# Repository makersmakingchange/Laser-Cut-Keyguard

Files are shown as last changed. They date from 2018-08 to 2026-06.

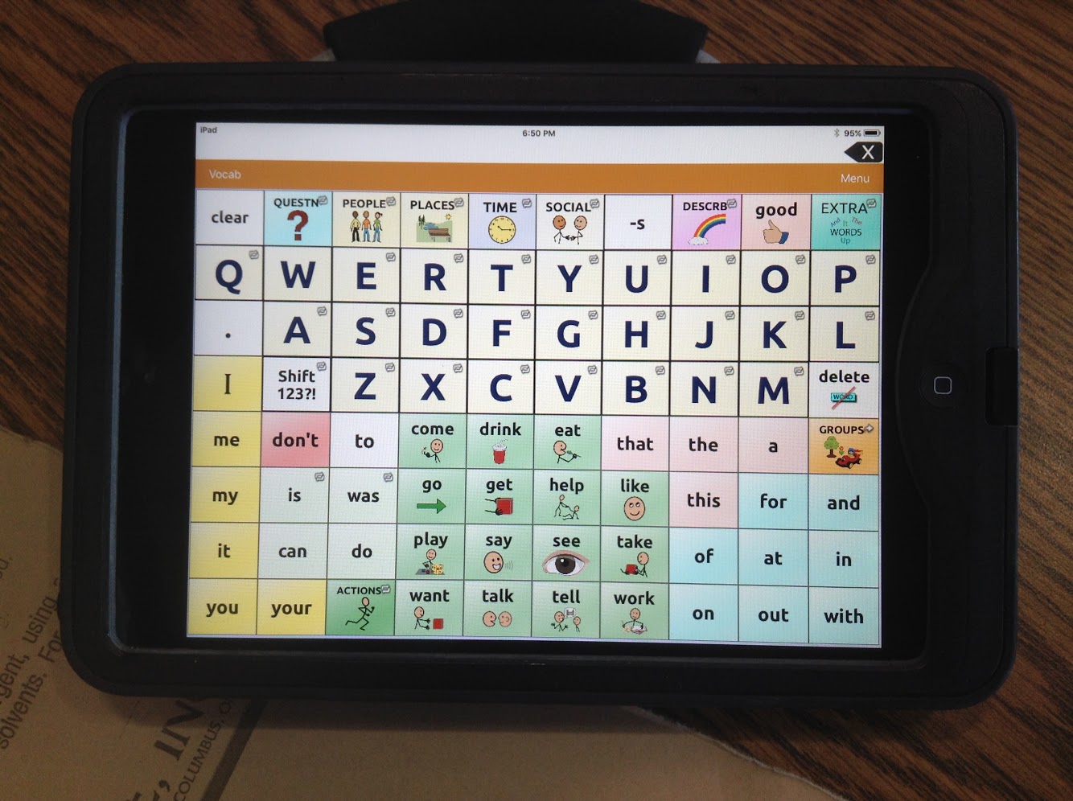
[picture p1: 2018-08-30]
Tablets/Wego7A_TouchChat WordPower_80/Wego7A_WordPower_80.JPG

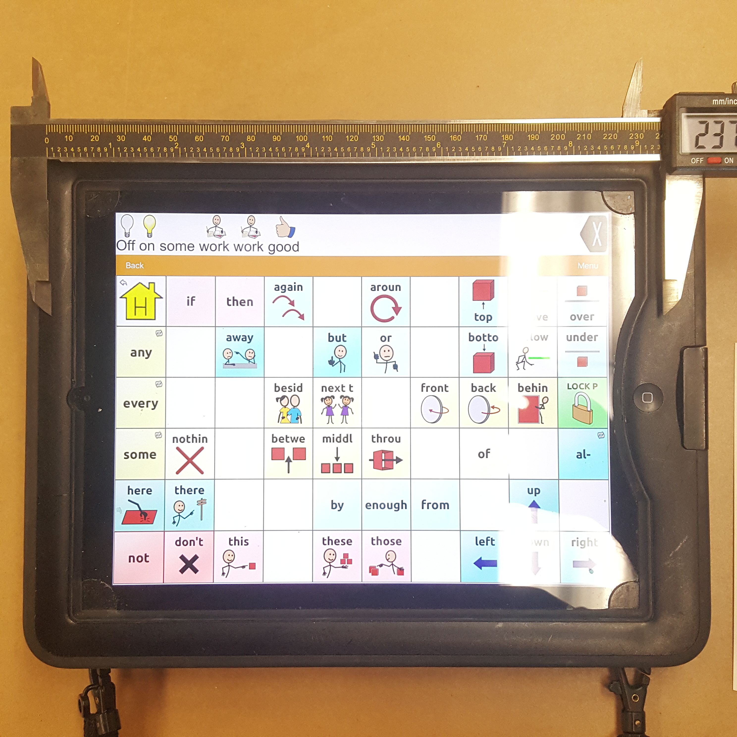
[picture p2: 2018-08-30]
Tablets/Wego10A_TouchChat WordPower_60/Wego10A_WordPower_60.jpg

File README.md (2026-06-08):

# Laser-Cut-Keyguard
Laser Cut Keyguards for AAC Devices and Keyboards

## Keyguards 
A keyguard is a thin plate that sits over top of a keyboard or an Alternate and Augmentative Communication (AAC) device. A keyguard may help a user use the keyboard or AAC device more easily and more effectively by helping them press buttons more accurately and helping support their hand or finger to reduce fatigue. 

## Makers Making Change Open Assistive Technology Design Library Link
https://www.makersmakingchange.com/product/laser-cut-keyguards/01tJR000000698iYAA 

## Tablets

| Device | Case | App        | Configuration | File | Notes |
|--------|:----:|------------|---------------|-------|------|
| iPad   | Big Grips Case    | Go Talk Now | 4      | https://github.com/makersmakingchange/Laser-Cut-Keyguard/blob/main/Tablets/iPad_GoTalkNOW_4/Big%20Grips%20Case/iPad_GoTalkNOW_4.svg      |      |
| iPad   | Otterbox      | Go Talk Now | 4        | https://github.com/makersmakingchange/Laser-Cut-Keyguard/blob/main/Tablets/iPad_GoTalkNOW_4/Otter%20Box%20Case/iPad_GoTalkNOW_4.svg      |      |
| iPad |  Life Proof Case | Touch Chat Word Power | 20  | https://github.com/makersmakingchange/Laser-Cut-Keyguard/blob/main/Tablets/iPad_TouchChat_20/iPad_TouchChat_20.svg      |      |
| iPad Mini 4 | TopEsct Kids Shockproof Handle Cover | Touch Chat Word Power | 42  | https://github.com/makersmakingchange/Laser-Cut-Keyguard/blob/main/Tablets/iPadMini4_TouchChat_42/iPadMini4_TouchChat_42.svg      |      |
| iPad Pro 9.7 | ChatWrap 10.2 | Touch Chat Word Power | 42  | https://github.com/makersmakingchange/Laser-Cut-Keyguard/blob/main/Tablets/iPadPro9-7_TouchChat_42/iPadPro9-7_TouchChat_42.svg      |      |
| Wego 7A |  Wego 7A Case | Touch Chat Word Power | 80  | https://github.com/makersmakingchange/Laser-Cut-Keyguard/blob/main/Tablets/Wego7A_TouchChat%20WordPower_80/Wego7A_WordPower_80.svg      |      |
| Wego 10A |  Wego 10A Case | Touch Chat Word Power | 60  | https://github.com/makersmakingchange/Laser-Cut-Keyguard/blob/main/Tablets/Wego10A_TouchChat%20WordPower_60/Wego10A_WordPower_60.svg      |      |

## Keyboards
| Device | Configuration | File | Notes |
|--------|---------------|-------|------|
| PSK3100 |               |       |      |
|        |               |       |      |
|        |               |       |      |

## Templates
| Device | File | Notes |
|--------|-------|------|
| iPad | https://github.com/makersmakingchange/Laser-Cut-Keyguard/blob/main/Templates/iPad.svg  |  |
| iPad2 | https://github.com/makersmakingchange/Laser-Cut-Keyguard/blob/main/Templates/iPad%202nd%20Gen.svg  |  |
| iPad 3rd generation | https://github.com/makersmakingchange/Laser-Cut-Keyguard/blob/main/Templates/iPad%203rd%20Gen.svg |  |
| iPad 4th generation | https://github.com/makersmakingchange/Laser-Cut-Keyguard/blob/main/Templates/iPad%204th%20Gen.svg |  |
| iPad 5th generation | https://github.com/makersmakingchange/Laser-Cut-Keyguard/blob/main/Templates/iPad%205th%20Gen.svg |  |
| iPad Pro 9.7-inch | https://github.com/makersmakingchange/Laser-Cut-Keyguard/blob/main/Templates/iPad%20Pro%209_7.svg |  |
| iPad Pro 10.5-inch | https://github.com/makersmakingchange/Laser-Cut-Keyguard/blob/main/Templates/iPad%20Pro%2010_5.svg |  |
| iPad Pro 12.9-inch 1st Generation | https://github.com/makersmakingchange/Laser-Cut-Keyguard/blob/main/Templates/iPad%20Pro%2012_9%201st%20Gen.svg  |  |
| iPad Pro 12.9-inch 2nd Generation | https://github.com/makersmakingchange/Laser-Cut-Keyguard/blob/main/Templates/iPad%20Pro%2012_9%202nd%20Gen.svg   |  |
| iPad mini | https://github.com/makersmakingchange/Laser-Cut-Keyguard/blob/main/Templates/iPad%20Mini.svg |  |
| iPad mini 2 | https://github.com/makersmakingchange/Laser-Cut-Keyguard/blob/main/Templates/iPad%20MIni%202.svg |  |
| iPad mini 3 | https://github.com/makersmakingchange/Laser-Cut-Keyguard/blob/main/Templates/iPad%20Mini%203.svg |  |
| iPad mini 4 | https://github.com/makersmakingchange/Laser-Cut-Keyguard/blob/main/Templates/iPad%20Mini%204.svg |  |
| iPad Air | https://github.com/makersmakingchange/Laser-Cut-Keyguard/blob/main/Templates/iPad%20Air.svg |  |
| iPad Air 2 | https://github.com/makersmakingchange/Laser-Cut-Keyguard/blob/main/Templates/iPad%20Air%202.svg |  |

NOTE: All designs in millimeters.

<!-- ABOUT MMC START -->
## About Makers Making Change
[Makers Making Change Logo](https://www.makersmakingchange.com/)

Makers Making Change is a program of [Neil Squire](https://www.neilsquire.ca/), a Canadian non-profit that uses technology, knowledge, and passion to empower people with disabilities.

Makers Making Change leverages the capacity of community based Makers, Disability Professionals and Volunteers to develop and deliver affordable Open Source Assistive Technologies.

 - Website: [www.MakersMakingChange.com](https://www.makersmakingchange.com/)
 - GitHub: [makersmakingchange](https://github.com/makersmakingchange)
 - Bluesky: [@makersmakingchange.bsky.social](https://bsky.app/profile/makersmakingchange.bsky.social)
 - Instagram: [@makersmakingchange](https://www.instagram.com/makersmakingchange)
 - Facebook: [makersmakechange](https://www.facebook.com/makersmakechange)
 - LinkedIn: [Neil Squire Society](https://www.linkedin.com/company/neil-squire-society/)
 - Thingiverse: [makersmakingchange](https://www.thingiverse.com/makersmakingchange/about)
 - Printables: [MakersMakingChange](https://www.printables.com/@MakersMakingChange)

### Contact Us
For technical questions, to get involved, or to share your experience we encourage you to [visit our website](https://www.makersmakingchange.com/) or [contact us](https://www.makersmakingchange.com/s/contact).
<!-- ABOUT MMC END -->

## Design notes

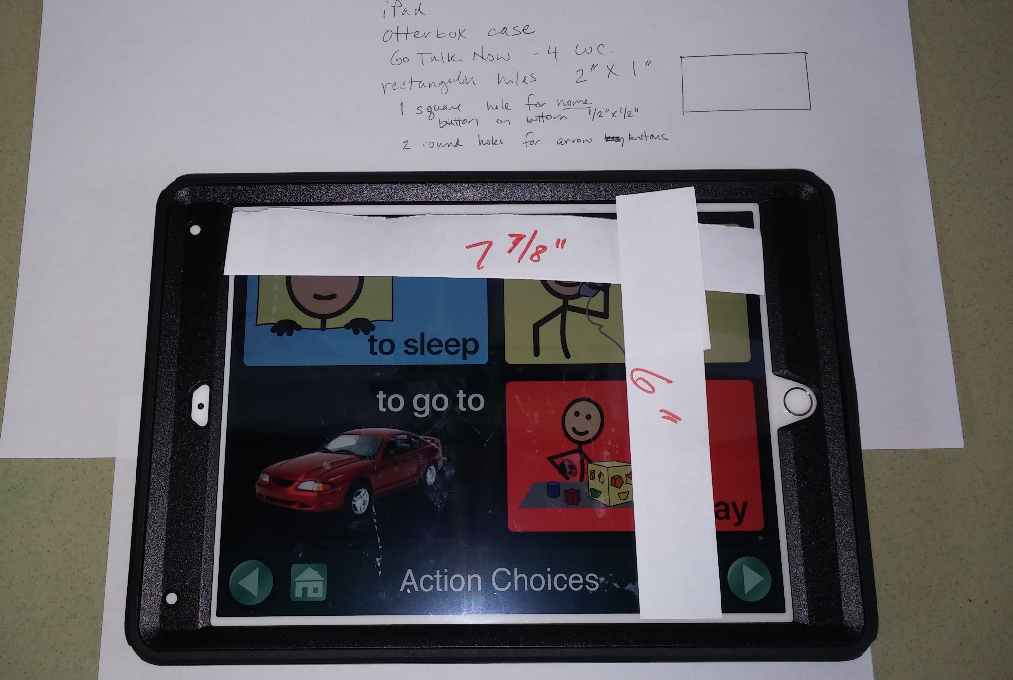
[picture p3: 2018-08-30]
Tablets/iPad_GoTalkNOW_4/Otter Box Case/iPad_GoTalkNOW_4.jpg

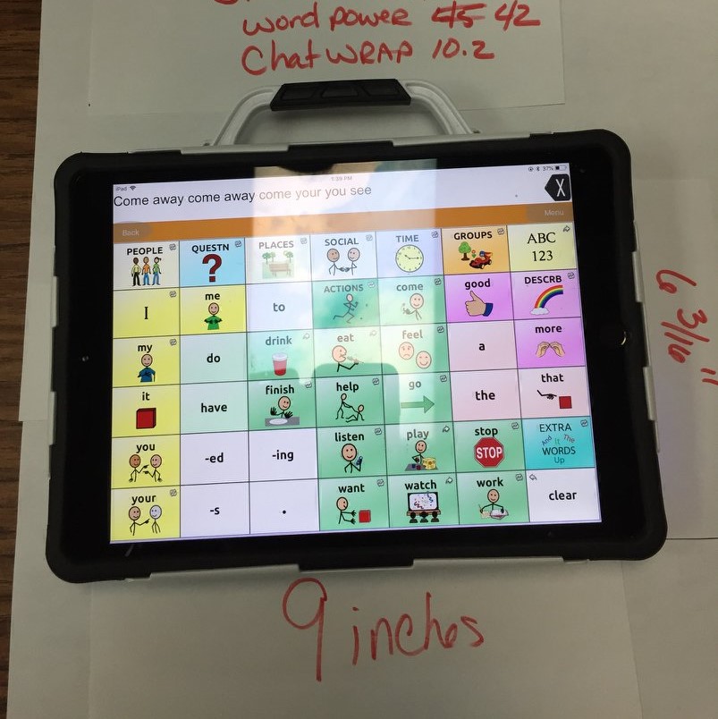
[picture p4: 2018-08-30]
Tablets/iPadPro9-7_TouchChat_42/iPadPro9-7_TouchChat_42.jpg

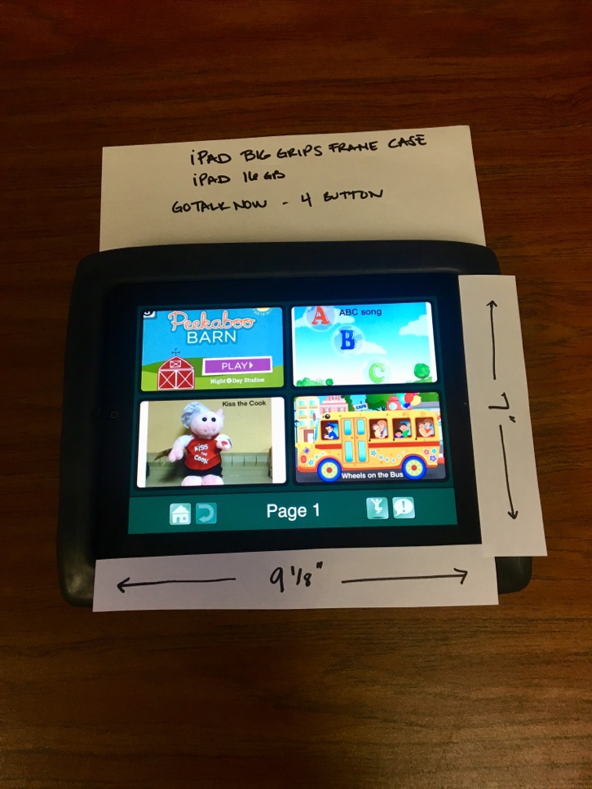
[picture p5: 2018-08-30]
Tablets/iPad_GoTalkNOW_4/Big Grips Case/iPadGoTalkNOW_4.jpg

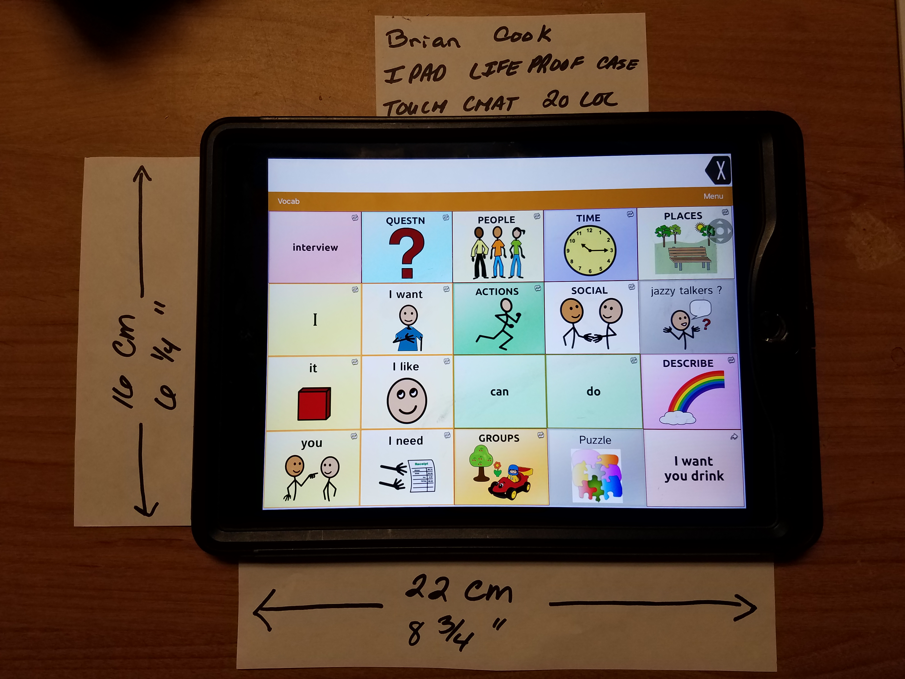
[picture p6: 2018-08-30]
Tablets/iPad_TouchChat_20/iPad_TouchChat_20.jpg

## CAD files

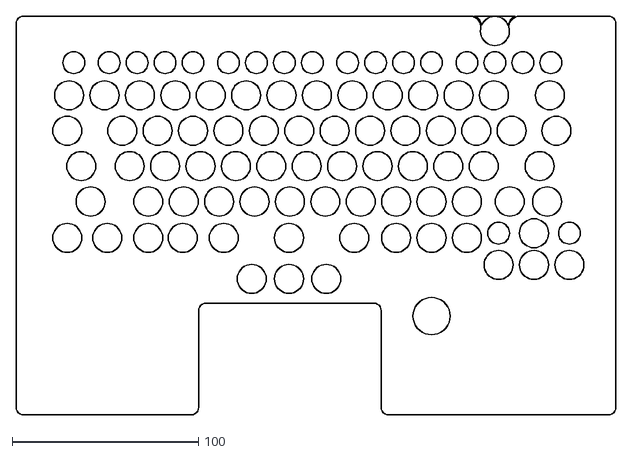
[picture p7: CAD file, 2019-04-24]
Keyboards/thinkpad-x1-carbon-6th-gen/thinkpad-x1-carbon-6th-gen.dxf
322.0 x 214.0

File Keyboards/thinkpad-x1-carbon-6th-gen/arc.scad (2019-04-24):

module arc(radius, thick, angle){
	intersection(){
		union(){
			rights = floor(angle/90);
			remain = angle-rights*90;
			if(angle > 90){
				for(i = [0:rights-1]){
					rotate(i*90-(rights-1)*90/2){
						polygon([[0, 0], [radius+thick, (radius+thick)*tan(90/2)], [radius+thick, -(radius+thick)*tan(90/2)]]);
					}
				}
				rotate(-(rights)*90/2)
					polygon([[0, 0], [radius+thick, 0], [radius+thick, -(radius+thick)*tan(remain/2)]]);
				rotate((rights)*90/2)
					polygon([[0, 0], [radius+thick, (radius+thick)*tan(remain/2)], [radius+thick, 0]]);
			}else{
				polygon([[0, 0], [radius+thick, (radius+thick)*tan(angle/2)], [radius+thick, -(radius+thick)*tan(angle/2)]]);
			}
		}
		difference(){
			circle(radius+thick);
			circle(radius);
		}
	}
}

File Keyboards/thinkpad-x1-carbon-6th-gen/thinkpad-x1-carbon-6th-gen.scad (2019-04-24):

include <arc.scad>

material_thickness=3;
plate_y_size = 214;
plate_x_size = 322;
corner_radius = 4;

key_hole_diameter=15.6;
fn_hole_diameter=11.7;
fingerprint_diameter = 20;
//oval_key_diameter_x = key_hole_diameter;
//oval_key_diameter_y = fn_hole_diameter;
//backspace_key_diameter_x = 30;

row1_y_offset = -8;
row2_y_offset = -25;
row3_y_offset = -42.5;
row4_y_offset = -61.5;
row5_y_offset = -80.5;
row6_y_offset = -99.5;
row7_y_offset = -119;
row8_y_offset = -141;
motion_y_offset = -123.5;
trackpad_y_offset = -154;
fingerprint_y_offset = -161;

row1_power_switch_offset=257;

row2_esc_offset = 31;
row2_f1_offset = 50;
row2_pitch = 15;
row2_f5_offset = row2_f1_offset + 64;
row2_f9_offset = row2_f5_offset + 64;
row2_home_offset = row2_f9_offset + 64;
row2_delete_offset = row2_home_offset + 45;

row3_key_offset = 28.5;
row3_key_pitch = 19;
row3_key_count = 13;
row3_backspace_pitch = 30;

row4_tab_offset = 27.5;
row4_key_offset = 57;
row4_key_pitch = 19;
row4_key_count = 12;
row4_backslash_pitch = 24;

row5_caps_offset = 35;
row5_key_offset = 61;
row5_key_pitch = 19;
row5_key_count = 11;
row5_enter_pitch = 30;

row6_lshift_offset = 40;
row6_key_offset = 71;
row6_key_pitch = 19;
row6_key_count = 10;
row6_rshift1_pitch = 23;
row6_rshift2_pitch = 43;

row7_fn_offset = 27.5;
row7_ctrl1_offset = 49;
row7_meta_offset = 71;
row7_alt1_offset = 89.5;
row7_space2_offset = 146.5;
row7_space1_offset = row7_space2_offset-35;
row7_space3_offset = row7_space2_offset+35;
row7_alt2_offset = 204;
row7_prtsc_offset = 223;
row7_ctrl2_offset = 242;

row8_centremouse_offset = 146.5;
row8_leftmouse_offset = row8_centremouse_offset-20;
row8_rightmouse_offset = row8_centremouse_offset+20;

motion_x_offset = 278;
motion_x_spacing = 19;
motion_y_upper = 7;
motion_y_lower = 10;

trackpad_loffset = 98;
trackpad_roffset = 196;

fingerprint_offset = 223;

$fn=36;

module row1() {
    translate([row1_power_switch_offset,0]) circle(d=key_hole_diameter, $fn=36);
    translate([row1_power_switch_offset-key_hole_diameter/2-corner_radius-1.75, key_hole_diameter/2-corner_radius-1.75]) rotate([0,0,45]) arc(corner_radius+2, 0.5, 90);
    translate([row1_power_switch_offset+key_hole_diameter/2+corner_radius+1.75, key_hole_diameter/2-corner_radius-1.75]) rotate([0,0,135]) arc(corner_radius+2, 0.5, 90);}

module function_keys(count) {
    for(ix =[0:count-1]) {
        translate([ix*row2_pitch,0]) circle(d=fn_hole_diameter, $fn=36);
    }
}

module row2() {
    translate([row2_esc_offset,0]) circle(d=fn_hole_diameter, $fn=36);
    
    translate([row2_f1_offset,0]) function_keys(4);
    translate([row2_f5_offset,0]) function_keys(4);
    translate([row2_f9_offset,0]) function_keys(4);
    translate([row2_home_offset,0]) function_keys(3);
    translate([row2_delete_offset,0]) function_keys(1);
}

module row3() {
    for(ix = [0:row3_key_count-1]) {
        translate([row3_key_offset+ix*row3_key_pitch,0]) circle(d=key_hole_diameter, $fn=36);
    }
    translate([row3_key_offset+(row3_key_count-1)*row3_key_pitch+row3_backspace_pitch,0]) circle(d=key_hole_diameter, $fn=36);
}

module row4() {
    translate([row4_tab_offset,0]) circle(d=key_hole_diameter, $fn=36);
    for(ix = [0:row4_key_count-1]) {
        translate([row4_key_offset+ix*row4_key_pitch,0]) circle(d=key_hole_diameter, $fn=36);
    }
    translate([row4_key_offset+(row4_key_count-1)*row4_key_pitch+row4_backslash_pitch,0]) circle(d=key_hole_diameter, $fn=36);
}

module row5() {
    translate([row5_caps_offset,0]) circle(d=key_hole_diameter, $fn=36);
    for(ix = [0:row5_key_count-1]) {
        translate([row5_key_offset+ix*row5_key_pitch,0]) circle(d=key_hole_diameter, $fn=36);
    }
    translate([row5_key_offset+(row5_key_count-1)*row5_key_pitch+row5_enter_pitch,0]) circle(d=key_hole_diameter, $fn=36);
}

module row6() {
    translate([row6_lshift_offset,0]) circle(d=key_hole_diameter, $fn=36);
    for(ix = [0:row6_key_count-1]) {
        translate([row6_key_offset+ix*row6_key_pitch,0]) circle(d=key_hole_diameter, $fn=36);
    }
    translate([row6_key_offset+(row6_key_count-1)*row6_key_pitch+row6_rshift1_pitch,0]) circle(d=key_hole_diameter, $fn=36);
    translate([row6_key_offset+(row6_key_count-1)*row6_key_pitch+row6_rshift2_pitch,0]) circle(d=key_hole_diameter, $fn=36);
}

module row7() {
    translate([row7_fn_offset,0]) circle(d=key_hole_diameter, $fn=36);
    translate([row7_ctrl1_offset,0]) circle(d=key_hole_diameter, $fn=36);
    translate([row7_meta_offset,0]) circle(d=key_hole_diameter, $fn=36);
    translate([row7_alt1_offset,0]) circle(d=key_hole_diameter, $fn=36);
    translate([row7_space1_offset,0]) circle(d=key_hole_diameter, $fn=36);
    translate([row7_space2_offset,0]) circle(d=key_hole_diameter, $fn=36);
    translate([row7_space3_offset,0]) circle(d=key_hole_diameter, $fn=36);
    translate([row7_alt2_offset,0]) circle(d=key_hole_diameter, $fn=36);
    translate([row7_prtsc_offset,0]) circle(d=key_hole_diameter, $fn=36);
    translate([row7_ctrl2_offset,0]) circle(d=key_hole_diameter, $fn=36);
}

module row8() {
    translate([row8_leftmouse_offset,0]) circle(d=key_hole_diameter, $fn=36);
    translate([row8_centremouse_offset,0]) circle(d=key_hole_diameter, $fn=36);
    translate([row8_rightmouse_offset,0]) circle(d=key_hole_diameter, $fn=36);
}

module motion() {
    // up arrow
    translate([0, +motion_y_upper]) circle(d=key_hole_diameter, $fn=36);
    // pgup
    translate([-motion_x_spacing, +motion_y_upper]) circle(d=fn_hole_diameter, $fn=36);
    // pgdn
    translate([+motion_x_spacing, +motion_y_upper]) circle(d=fn_hole_diameter, $fn=36);
    // down arrow
    translate([0, -motion_y_lower]) circle(d=key_hole_diameter, $fn=36);
    // left arrow
    translate([-motion_x_spacing, -motion_y_lower]) circle(d=key_hole_diameter, $fn=36);
    // right arrow
    translate([+motion_x_spacing, -motion_y_lower]) circle(d=key_hole_diameter, $fn=36);
}

difference() {
    union() {
        hull() {
            translate([+corner_radius, -corner_radius]) circle(r=corner_radius, $fn=24);
            translate([plate_x_size-corner_radius, trackpad_y_offset]) circle(r=corner_radius, $fn=24);
            translate([plate_x_size-corner_radius, -corner_radius]) circle(r=corner_radius, $fn=24);
            translate([+corner_radius, trackpad_y_offset]) circle(r=corner_radius, $fn=24);
        }
        hull() {
            translate([+corner_radius, trackpad_y_offset+corner_radius]) circle(r=corner_radius, $fn=24);
            translate([trackpad_loffset-corner_radius, trackpad_y_offset+corner_radius]) circle(r=corner_radius, $fn=24);
            translate([+corner_radius, -plate_y_size+corner_radius]) circle(r=corner_radius, $fn=24);
            translate([trackpad_loffset-corner_radius, -plate_y_size+corner_radius]) circle(r=corner_radius, $fn=24);
        }
        hull() {
            translate([trackpad_roffset+corner_radius, trackpad_y_offset+corner_radius]) circle(r=corner_radius, $fn=24);
            translate([trackpad_roffset+corner_radius, -plate_y_size+corner_radius]) circle(r=corner_radius, $fn=24);
            translate([plate_x_size-corner_radius, trackpad_y_offset+corner_radius]) circle(r=corner_radius, $fn=24);
            translate([plate_x_size-corner_radius, -plate_y_size+corner_radius]) circle(r=corner_radius, $fn=24);
        }
    }    

    translate([0,row1_y_offset]) row1();
    translate([0,row2_y_offset]) row2();
    translate([0,row3_y_offset]) row3();
    translate([0,row4_y_offset]) row4();
    translate([0,row5_y_offset]) row5();
    translate([0,row6_y_offset]) row6();
    translate([0,row7_y_offset]) row7();
    translate([0,row8_y_offset]) row8();
    translate([motion_x_offset, motion_y_offset]) motion();
    translate([fingerprint_offset, fingerprint_y_offset]) circle(d=fingerprint_diameter, $fn=36);
    hull() {
        translate([trackpad_loffset+corner_radius,trackpad_y_offset-corner_radius]) circle(r=corner_radius, $fn=24);
        translate([trackpad_roffset-corner_radius,trackpad_y_offset-corner_radius]) circle(r=corner_radius, $fn=24);
    }
}

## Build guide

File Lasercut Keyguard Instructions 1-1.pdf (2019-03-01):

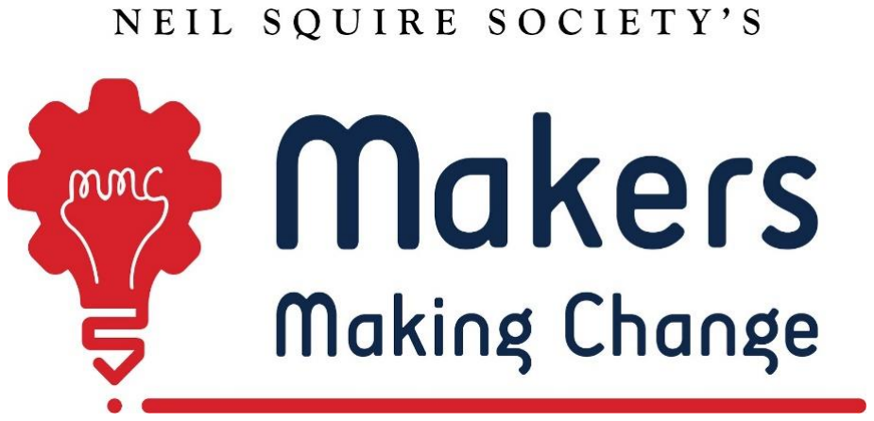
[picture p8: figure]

# Laser Cut Keyguard Instructions

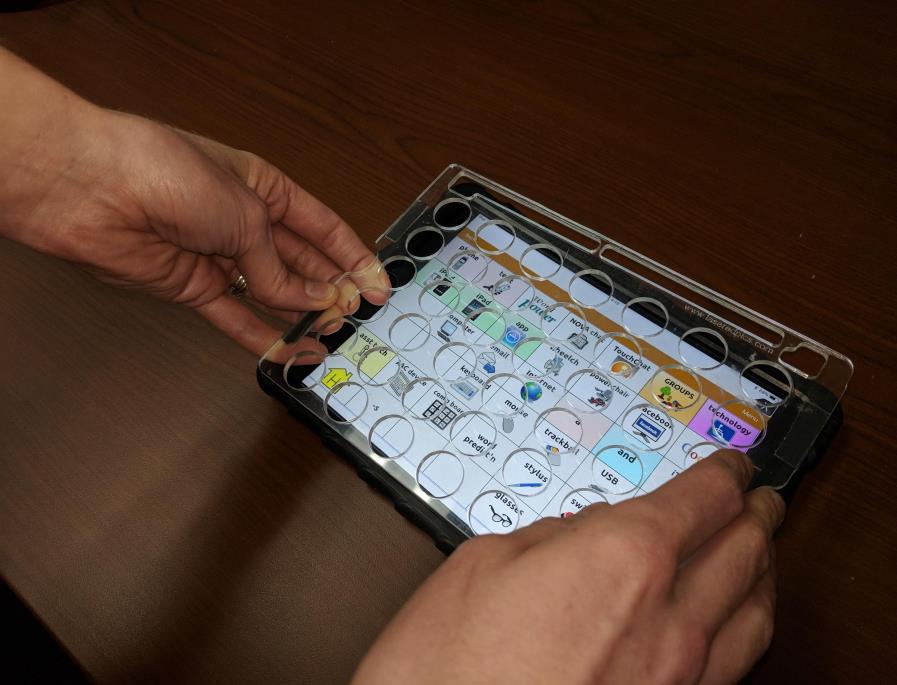
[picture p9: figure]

This guide describes a workflow to assist a maker to design a custom lasercut keyguard for an Augmentative and Alternate Communication (AAC) device.

An AAC device is used to help someone communicate. AAC devices may be comprised of a variety of different tablets, (tablet cases) and apps. The AAC apps may also provide options to customize the number, size and layout.

A keyguard is a thin plate that sits over top of an AAC device. The keyguard can help a user use the AAC device more easily and more effectively. The openings in the keyguard can help provide focus, tactile feedback, and the ability to rest the user’s hand on the device without activating a button, reducing fatigue.

Laser Cut Keyguard

Version 0.2 | www.makersmakingchange.com | 2/17

## Contents

Overview | 3
Equipment | 3
1. Gathering Device Information | 3
Usage | 3
Device Measurements | 4
Capturing A Reference Image | 4
Using The Reference Image | 6
Scaling | 6

### 2. Keyguard Layout | 7

Design Considerations | 7
Keyguard Design | 7
Marking | 7
Customization / Personalization | 8
Laser Cutter File Preparation | 8
Data Transfer | 9

### 3. Test-cut | 9

Laser Test Cut | 10
Assessing Fit | 10
Refinements | 10

### 4. Final Cut | 10

Final Design Checks | 10
Laser Cutting | 10
5. Finishing | 10
Smoothing | 10
Mounting | 10
Appendix | 12
iPad Screenshot Scaling | 12
Fusion 360 Workflow | 13
SolidWorks Workflow | 15
Insert Sketch Picture | 15
Additional Resources | 17

# Overview

The overall process involves measuring the users device, designing the layout of the Keyguard, preparing the vector file for Laser cutting, Laser cutting the Keyguard, and mounting the Keyguard.

# Equipment

Creating a custom lasercut keyguard requires the following items:
- Computer with vector graphics software.
- Inkscape
- (Optional) CAD Software (Autodesk Fusion 360, SolidWorks)
- Measuring Tools
- Ruler
- Measuring Tape
- Keyguard Material
- Cardstock or cardboard to test fit
- 1/8 in. or 1/16 in. acrylic
- Mounting
- Suction tape

These instructions will refer to steps in Inkscape, but alternative vector graphic software such as Adobe Illustrator or Corel Draw may also be used.

# 1.Gathering Device Information

The first step is to gather information about how the user uses their device and then get the physical size of the device and app to create an appropriate keyguard.

## Usage

Does the user want access to the on-screen buttons for editing, menu, iPad home button, etc., or is the keyguard to block access?

What size and shape of openings are required?

Should any additional information be marked on the keyguard?

## Device Measurements

If the user’s device and AAC application is available, measurements can be made directly. This is the preferred method for a number of reasons:
- You can measure the device directly, and take into considerations such as mounting in the case and size of holes for fingers.
- You can do a test cut on low cost material like card stock and cardboard and see the fit and alignment. You don’t have to get it perfect on the first try.
- You meet the person you are helping. It is incredibly rewarding for both the maker and the disability professional/person using the device to see the creation process and to have a solution on hand.

In some cases, the user may submit a photo of the device with some measurements that can be used to scale and determine the measurements. What is below is some notes for that.

## Capturing A Reference Image

To accurately measure the position of the various buttons, it can be helpful to capture a reference image. To ensure the final keyguard properly fits the device and the openings match the buttons, it is critical that the AAC used is sent, along with the exact iPad / tablet device, to ensure the keyguard fits for the user’s device and app combonation.

To capture a reference image for the app, a screen shot of the device running the app is critical for the layout. We have found pictures from phones, with measurements or tape over the device, have issues with scaling and small errors that make the keyguard close, but not good enough.

Take screen shot of the device with the app running and the piece of paper. Try to position the camera so the device is not skewed. This is often down on iPads by
1. Press and hold the Sleep/Wake (on/off) button on the top of your iPad.
2. Quickly click the Home button at the bottom of the screen.
3. Release both buttons.

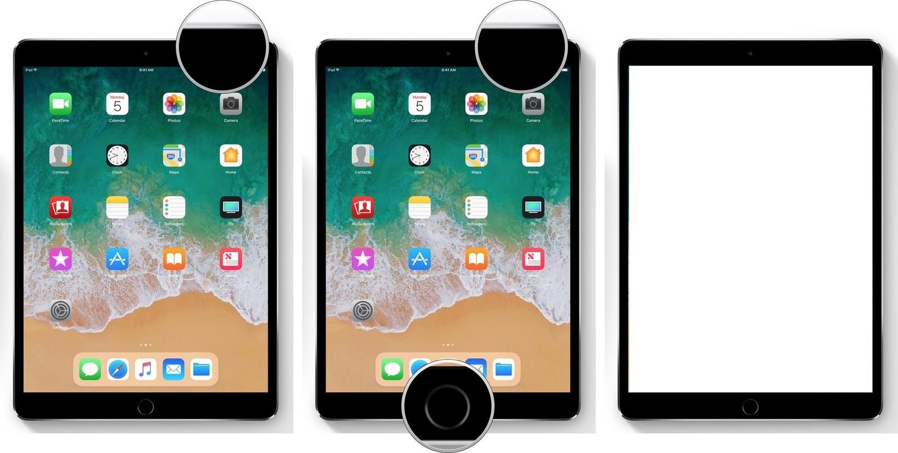
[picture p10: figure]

Some tablets and newer versions of iOS devices have other ways to take screenshots. You may need to google your specific device to see how to best take a screenshot.

## Using The Reference Image

In order to use a device photo to design the keyguard layout, the image needs to be rotated and scaled.

Import Reference Image
1. Open Inkscape.
2. Select File > Import
3. Select the reference image. Press Open.
4. Press OK to use the default import options.

Rotation
Rotate the photo so that the tops and sides are aligned with the horizontal and vertical axes.

Tip: Use the measuring tool (ruler icon on toolbar, or ‘M’ on the keyboard) to measure the angle of part of the image that should be horizontal.

It is also critical to know the exact model of the iPad / tablet being used. This information is important as the screen size varies by device, as well as to make sure there are cut outs for the camera, home button, etc. The infromation on the make and model can often be found on the back of the device.

A repository of iPad device layouts to start your design can be found and downloaded from Maker Making Change’s github library.

https://github.com/makersmakingchange/Laser-Cut-Keyguard/tree/master/Templates

Scaling

Scale the image so that the size of the image on the computer matches the size of the device. Often, screenshots come at 1024 pixels wide and 768 pixels high regardless of the actual size of the screen on the device.

Use the measuring tool to measure the known distance in the reference photo. Change the units to match the known measurement. Pleae refer to the Appendix at the end of this document to convert your picture to the measurement in millimeters (mm) so that your keyguard fits the device.

5/25 * 100 = 20%

1. Click Object > Transform
2. Click on the Scale tab.
3. Make sure the ‘Scale Proportionally’ is checked.
4. Enter the scale factor calculated from the appendix.
5. Click Apply to scale the image.

# 2. Keyguard Layout

## Design Considerations

Message Window Size Settings
Many AAC applications have a message window near the top of the screen. This message window may be adjustable to allow the user to set the number of lines and the text size. Changing the message window size affects the size of the buttons below. Increasing the number of lines or text size of the message window will cause the cause the buttons below to reduce in height.

Camera Access
Don’t cover the camera.

Symmetry
In some cases, it can be helpful to make the keyguard symmetric about a vertical axis so that the device can be rotated.

Material Thickness
Thicker keyguards may help reduce the number of accidental touches.

Robustness
Round the corners of the keyguard to remove the sharp edges.

Try to avoid skinny section, especially near the edges, that may cause the keyguard to crack or break.

Mounting
How will the keyguard be mounted to the device?

## Keyguard Design

Using the reference image as a reference, add rectangles and circles to match the outline and the openings for the keyguard.

TIP: Use rectangles and circles and set the dimensions using the top bar.

## Marking

Adding some laser etched marking can make the keyguard easier to use for the user, caregiver, or therapist, by helping identity for which app, device and/or user the keyguard belongs.

One way to add text that is fast to etch as lines with the laser cutter is to use the Hershey Text plugin in Inkscape:

1. Extensions > Render > Hershey Text
2. In the Hershey Text dialog box:
a. Type in desired text
b. Select Action: Typeset that text
c. Select Font Face: Sans-1 stroke
3. Click Apply.
4. Adjust the size and position of the text as desired.

This will create a single-stroke vector path that can be quickly etched using the laser cutter.

Use these steps to add “makersmakingchange.com” near an edge of the keyguard. In order to be legible, the text should be ⅛ inch (3 - 4 mm) in height. This will allow the user to locate the plans for a replacement or request a modification to their keyguard and provide an opportunity for other potential keyguard users to request their own keyguard.

## Customization / Personalization

Add any additional information requested by the user to the keyguard. This may include, for example:
- Name
- Organization
- Phone number
- App / App setting
- Etc

Try to position the text in a location so that it will not obscure the screen. The space on either side of the camera or Home button is usually a good choice.

## Laser Cutter File Preparation

Once the geometry of the keyguard has been finalized, the next step is to prepare the design for laser cutting. These instructions may vary depending on the laser cutter and laser cutter software.

Operation | Stroke | Fill | Width
Cut Line | Red (R:255,G:0,B:0) | None | 0.01mm

Engrave Line | Blue (R:0,G:0,B:255) | None | 0.01mm
Engrave Area | None | Black (R:0,G:0,B:0) | 0

Cut lines are meant to cut through the entire depth of the material. The outside outline and all of the button openings should be set as Cut Lines.

Engrave lines will engrave a line a limited depth. Single-line text markings should be set as Engrave Lines.

Engrave Area will engrave a closed area. This can be useful for adding closed shapes, but takes longer to do on the laser cutter.

Save the design file using the following naming convention: {FirstName}{LastInitial}{Number}_{Revision}.svg

Save a copy as a PDF for laser cutting using the same naming convention: {FirstName}{LastInitial}{Number}_{Revision}.pdf

For example, the initial design for John Smith’s first keyguard should be saved as: JohnS01_1.svg
AND
JohnS01_1.pdf

## Data Transfer

Transfer both the SVG and PDF file to a USB flash drive.

# 3. Test-cut

This is a recommended but optional step.

Before cutting the keyguard out of plastic, it is helpful to test the fit to see how well the design matches up on the device and how well the openings match up to the buttons on the application. To quickly and inexpensively test the fit, we can laser cut the keyguard out of cardstock or cardboard.

## Laser Test Cut

Bring the USB stick with the PDF design file to the laser cutter.

## Assessing Fit

The keyguard should sit flat on the touchscreen. A little wiggle room is better than too tight. The openings should match up with the buttons

## Refinements

If necessary, adjust the size and spacing so the keyguard fits the device and matches the buttons properly.

# 4. Final Cut

## Final Design Checks

□ | If possible, have you cut a design to test the fit?
□ | Are the corners rounded?
□ | Is the keyguard marked with makersmakingchange.com ?
□ | Is the keyguard marked with any requests from the user (name, app, etc)?

## Laser Cutting

Bring the USB flash drive with the final design files to the laser cutter so the keyguard can be cut out of acrylic.

# 5.Finishing

There are a few final steps to make the keyguard ready for use.

## Smoothing

Check to make sure there are no sharp edges on the keyguard outline or any of the openings. A sharp knife or small file can be used to smooth over any sharp edges.

## Mounting

There are a few different methods for mounting a keyguard on to an AAC device including:
- suctions cups

- velcro
- suction tape (such as UGLu - https://www.amazon.com/MTR100-UGLU-Glue-Strips/dp/B001KFY7EY) (https://www.amazon.com/MTR100-UGLU-Glue-Strips/dp/B001KFY7EY)
- magnets
- under the case

Suction tape (or "suction cup tape") bonds to smooth, flat, clean surfaces just like a suction cup. Though not actually suction cups, the surface of this tape has thousands of microscopic craters that work by creating many partial vacuums between the tape and the target surface.

The tape is not pressure sensitive, can re-bond repeatedly, and leaves no residue on the target surface. To remove, you simply pull the tape off or twist it to break the bond.

1. Cut some narrow strips of suction tape.
2. Attach the strips of suction tape to the edges of the keyguard.

# Appendix

## iPad Screenshot Scaling

To capture a screenshot on an iPad device, load the app and hold the device in the desired orientation. While holding down the On/Off button, press the Home button. The screen will flash to indicate a screenshot has been captured.

The screenshot image will be 1024 pixels wide and 768 pixels high regardless of the actual size of the screen on the device. In order to scale it properly, use the conversion factor in the table below.

iPad Type | Screen Width (mm) | Screen Height (mm) | Conversion (px to mm)
iPad | 198.1 | 149 | 0.193
iPad2 | 198.1 | 149 | 0.193
iPad 3rd generation | 198.1 | 149 | 0.193
iPad 4th generation | 198.1 | 149 | 0.193
iPad 5th generation | 196.47 | 147.39 | 0.192
iPad Pro 9.7-inch | 203.11 | 153.71 | 0.198
iPad Pro 10.5-inch | 213.5 | 160.13 | 0.208
iPad Pro 12.9-inch 1st Generation | 262.27 | 196.61 | 0.256
iPad Pro 12.9-inch 2nd Generation | 262.27 | 196.61 | 0.256
iPad mini | 161.2 | 121.3 | 0.157
iPad mini 2 | 161.2 | 121.3 | 0.157
iPad mini 3 | 161.2 | 121.3 | 0.157
iPad mini 4 | 161.24 | 121.31 | 0.157
iPad Air | 198.1 | 149 | 0.193
iPad Air 2 | 203.11 | 153.71 | 0.198

Source: http://volksswitch.org/index.php/volks-devices/fully-customizable-3d-printable-aac-keyguard-for-tablets/using-app-screenshots-to-determine-the-app-layout/ (http://volksswitch.org/index.php/volks-devices/fully-customizable-3d-printable-aac-keyguard-for-tablets/using-app-screenshots-to-determine-the-app-layout/)

For templates for the device that take into account the device dimensions, holes for the camera or home button, etc, please see this github repository of iPads. https://github.com/makersmakingchange/Laser-Cut-Keyguard/tree/master/Templates

## Fusion 360 Workflow

Autodesk Fusion 360 is a cloud-based, computer-assisted design program with a free license for hobbyists and enthusiasts. Fusion 360 requires a 64 bit system and either Windows or MAC OS. To access the hobbyist license, you’ll need to sign up for an account and download the free trial: https://www.autodesk.com/products/fusion-360/overview

Fusion 360 has a few features that make it a useful tool for designing custom laser cut keyguards.

Insert Canvas
1. Under the insert menu, select Insert Canvas
2. Choose the top plane
3. Select the image
4. Rotate the image to align the edges with the grid. You may need to manually enter a small value (e.g. 1, 0.1 degrees) into the box.

Scale the Image
1. In the Browser bar, click the triangle beside the Canvasses Folder to show its contents
2. Right click on the canvas image you added in the previous step and select ‘Calibrate Image’
3. Use the mouse to select a first and a second point on the image with a known distance between them, and then enter the distance value in to the dialog box. Try to be as accurate as possible when entering the points so the reference image is scaled properly.

Design Keyguard Layout
1. Create a new sketch on the same plane as the canvas.
2. Create the outline of the keyguard using the rectangle tool.
3. Create the keyguard button openings using rectangles or circles according to the users preference.
4. When finished, close the sketch.

Tip #1: Use construction lines to help align the openings.

Tip #2: To make the design symmetric, add a construction line in the middle and use the Sketch>Mirror tool to copy openings to the other side. You can also use Symmetry constraints to enforce symmetry.

Extrude Keyguard Sketch
1. Click Create > Extrude

2. Select the keyguard profile sketch.
3. Set the extrusion distance to 1/16 inch or 1/8 inch

Export sketch
1. Right click on the sketch
2. Click ‘Save as DXF’

Import sketch into Inkscape
1. Import the dxf file.
2. In some cases the design may be upside down. You may need to rotate the design 180 degrees.
3. Add any marking or text.
4. Change the line color and stroke according to the laser cut file preparation instructions.

## SolidWorks Workflow

### Insert Sketch Picture

To insert and resize a picture on a sketch plane:

1. In an open sketch, click Sketch Picture (Sketch toolbar) or click Tools > Sketch Tools > Sketch Picture.
2. In the dialog box, browse to the picture file and click Open.

When you insert a picture, the scale tool automatically displays.

The scale tool is a construction line with handles at each end. Use the scale tool to resize the picture.

You can also resize the picture in the graphics area by dragging its handles. You can drag the

picture without changing its size when the pointer changes to .

### 3. To use the scale tool:

a. Place the left end of the scale tool at one end of the picture. Zoom to position the scale tool and picture as needed.

The pointer changes to .

b. Drag the right end of the scale tool to extend the length of the line. You can also drag the right end to rotate the picture.

The pointer changes to .

c. In the Modify dialog box for dimensions, enter a value for the desired measurement and

click .

The picture and the scale tool resize together.

d. Clear Enable Scale Tool in the Property Manager to remove the construction line from the graphics area.
4. Continue to set properties in the Sketch Picture Property Manager and click .

Design Keyguard Layout
1. Create a new sketch on the same plane as the canvas.
2. Create the outline of the keyguard using the rectangle tool.
3. Create the keyguard button openings using rectangles or circles according to the users preference.
4. When finished, close the sketch.

Tip #1: Use construction lines to help align the openings.

Tip #2: To make the design symmetric, add a construction line in the middle and use the Sketch>Mirror tool to copy openings to the other side. You can also use Symmetry constraints to enforce symmetry.

Extrude Keyguard Sketch
1. Click Create > Extrude
2. Select the keyguard profile sketch.
3. Set the extrusion distance to 1/16 inch or 1/8 inch

Export DXF File

Option 1 File > Save As > DXF is the most general method. The dialog at the right requires several inputs from the user: Be sure to select a view that is normal to the flat part and deselect the others. The output alignment tools specify the X and Y axes and whether the part is flipped on an axis.

Option 2 For an inherently flat part or an unfolded sheet metal part, right click on the face and select Export to DXF/DWG from the context menu. In this case, there’s no dialog to select a view because the face determines the view. This workflow is a little faster.

Import sketch into Inkscape
1. Import the dxf file.
2. In some cases the design may be upside down. You may need to rotate the design 180 degrees.
3. Add any marking or text.
4. Change the line color and stroke according to the laser cut file preparation instructions.

## Additional Resources

Suction Tape
http://www.keyguardat.com/suction-tape/

3D Printed Keyguard Workflow http://volksswitch.org/index.php/volks-devices/fully-customizable-3d-printable-aac-keyguard-for-tablets/ (http://volksswitch.org/index.php/volks-devices/fully-customizable-3d-printable-aac-keyguard-for-tablets/)

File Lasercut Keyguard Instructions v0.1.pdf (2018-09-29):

# Laser Cut Keyguard Instructions

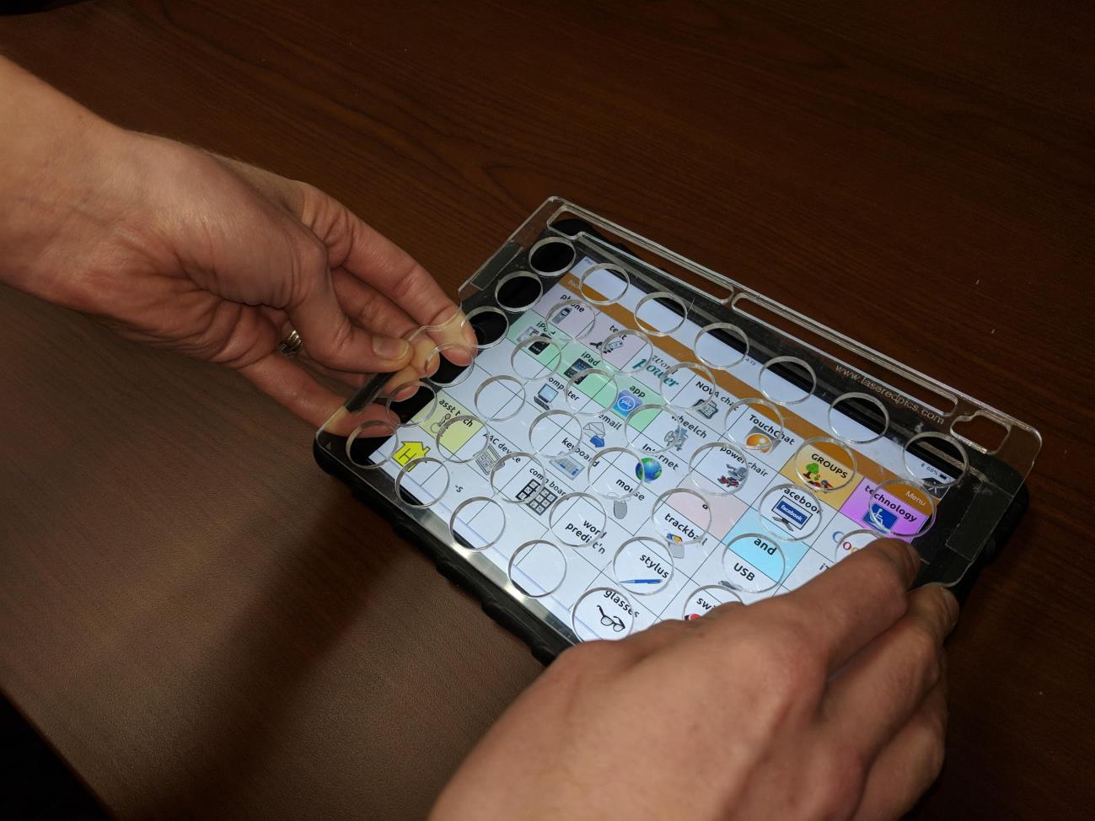
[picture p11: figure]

This guide describes a workflow to assist a maker to design a custom lasercut keyguard for an Augmentative and Alternate Communication (AAC) device.

An AAC device is used to help someone communicate. AAC devices may be comprised of a variety of different tablets, (tablet cases) and apps. The AAC apps may also provide options to customize the number, size and layout.

A keyguard is a thin plate that sits over top of an AAC device. The keyguard can help a user use the AAC device more easily and more effectively. The openings in the keyguard can help provide focus, tactile feedback, and the ability to rest the user’s hand on the device without activating a button, reducing fatigue.

Laser Cut Keyguard

Version 0.1 | www.makersmakingchange.com | 2/12

# Overview

The overall process involves measuring the users device, designing the layout of the Keyguard, preparing the vector file for Laser cutting, Laser cutting the Keyguard, and mounting the Keyguard.

# Equipment

Creating a custom lasercut keyguard requires the following items:
- Computer with vector graphics software.
- Inkscape
- (Optional) Autodesk Fusion 360
- Measuring Tools
- Ruler
- Measuring Tape
- Keyguard Material
- Cardstock or cardboard to test fit
- 1/8 in. or 1/16 in. acrylic
- Mounting
- Suction tape

These instructions will refer to steps in Inkscape, but alternative vector graphic software such as Adobe Illustrator or Corel Draw may also be used.

# 1.Gathering Device Information

The first step is to gather information about how the user uses their device and then get the physical size of the device and app to create an appropriate keyguard.

## Usage

Does the user want access to the on-screen buttons for editing, menu, iPad home button, etc., or is the keyguard to block access?

What size and shape of openings are required?

Should any additional information be marked on the keyguard?

## Device Measurements

If the user’s device and AAC application is available, measurements can be made directly.

In some cases, the user may submit a photo of the device with some measurements that can be used to scale and determine the measurements.

## Capturing A Reference Image

To accurately measure the position of the various buttons, it can be helpful to capture a reference image. To ensure the final keyguard properly fits the device and the openings match the buttons, it is critical that the reference image can be scaled properly.

To capture a reference image, accurately measure the cut a piece of paper to a length that spans the longest edge of the device. Accurately measure the length of the piece of paper and write it on the paper. It is important to know the distance of the screen opening to the closest milimeter or 1/16 inch.

Take an image of the device with the app running and the piece of paper. Try to position the camera so the device is not skewed.

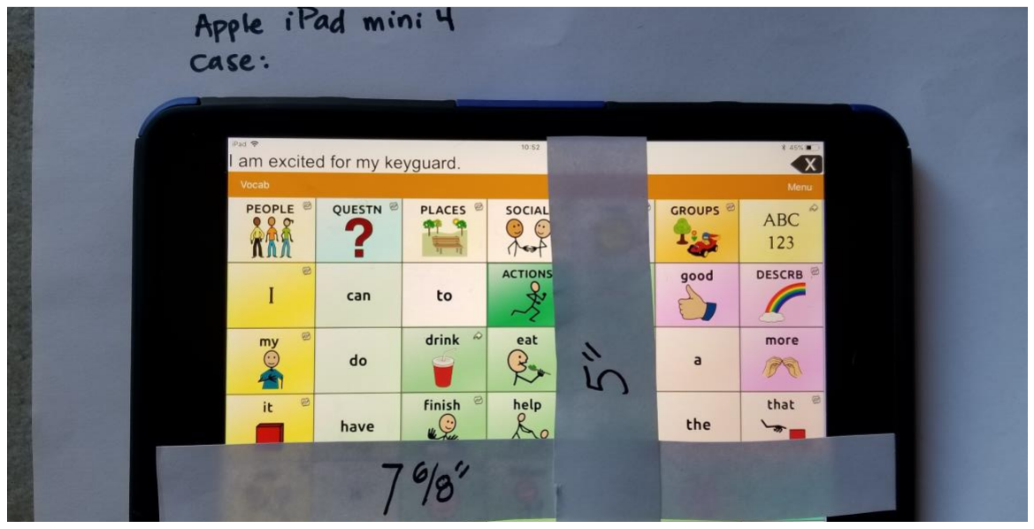
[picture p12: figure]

If possible, capture a screenshot of the image as well. See the appendix for instruction on how to capture a screenshot of the app.

## Using The Reference Image

In order to use a device photo to design the keyguard layout, the image needs to be rotated and scaled.

Import Reference Image
1. Open Inkscape.
2. Select File > Import
3. Select the reference image. Press Open.
4. Press OK to use the default import options.

Rotation
Rotate the photo so that the tops and sides are aligned with the horizontal and vertical axes.

Tip: Use the measuring tool (ruler icon on toolbar, or ‘M’ on the keyboard) to measure the angle of part of the image that should be horizontal.

Scaling

Scale the image so that the size of the image on the computer matches the size of the device.

Use the measuring tool to measure the known distance in the reference photo. Change the units to match the known measurement.

Calculate the required scaling factor by dividing the distance measured from the photo by the true distance measured on the device, then multiplying by 100.
For example, if the distance measured from the photo is 25 inches and the true distance is 5 inches, the scaling factor is:

5/25 * 100 = 20%

1. Click Object > Transform
2. Click on the Scale tab.
3. Make sure the ‘Scale Proportionally’ is checked.
4. Enter the scale factor calculated above.
5. Click Apply to scale the image.

# 2. Keyguard Layout

## Design Considerations

Message Window Size Settings
Many AAC applications have a message window near the top of the screen. This message window may be adjustable to allow the user to set the number of lines and the text size. Changing the message window size affects the size of the buttons below. Increasing the number of lines or text size of the message window will cause the cause the buttons below to reduce in height.

Camera Access
Don’t cover the camera.

Symmetry
In some cases, it can be helpful to make the keyguard symmetric about a vertical axis so that the device can be rotated.

Material Thickness
Thicker keyguards may help reduce the number of accidental touches.

Robustness
Round the corners of the keyguard to remove the sharp edges.

Try to avoid skinny section, especially near the edges, that may cause the keyguard to crack or break.

Mounting
How will the keyguard be mounted to the device?

## Keyguard Design

Using the reference image as a reference, add rectangles and circles to match the outline and the openings for the keyguard.

TIP: Use rectangles and circles and set the dimensions using the top bar.

## Marking

Adding some laser etched marking can make the keyguard easier to use for the user, caregiver, or therapist, by helping identity for which app, device and/or user the keyguard belongs.

One way to add text that is fast to etch as lines with the laser cutter is to use the Hershey Text plugin in Inkscape:

1. Extensions > Render > Hershey Text
2. In the Hershey Text dialog box:
a. Type in desired text
b. Select Action: Typeset that text
c. Select Font Face: Sans-1 stroke
3. Click Apply.
4. Adjust the size and position of the text as desired.

This will create a single-stroke vector path that can be quickly etched using the laser cutter.

Use these steps to add “makersmakingchange.com” near an edge of the keyguard. In order to be legible, the text should be ⅛ inch (3 - 4 mm) in height. This will allow the user to locate the plans for a replacement or request a modification to their keyguard and provide an opportunity for other potential keyguard users to request their own keyguard.

## Customization / Personalization

Add any additional information requested by the user to the keyguard. This may include, for example:
- Name
- Organization
- Phone number
- App / App setting
- Etc

Try to position the text in a location so that it will not obscure the screen. The space on either side of the camera or Home button is usually a good choice.

## Laser Cutter File Preparation

Once the geometry of the keyguard has been finalized, the next step is to prepare the design for laser cutting. These instructions may vary depending on the laser cutter and laser cutter software.

Operation | Stroke | Fill | Width
Cut Line | Red (R:255,G:0,B:0) | None | 0.01mm
Engrave Line | Blue (R:0,G:0,B:255) | None | 0.01mm

Engrave Area | None | Black (R:0,G:0,B:0) | 0

Cut lines are meant to cut through the entire depth of the material. The outside outline and all of the button openings should be set as Cut Lines.

Engrave lines will engrave a line a limited depth. Single-line text markings should be set as Engrave Lines.

Engrave Area will engrave a closed area. This can be useful for adding closed shapes, but takes longer to do on the laser cutter.

Save the design file using the following naming convention: {FirstName}{LastInitial}{Number}_{Revision}.svg

Save a copy as a PDF for laser cutting using the same naming convention: {FirstName}{LastInitial}{Number}_{Revision}.pdf

For example, the initial design for John Smith’s first keyguard should be saved as: JohnS01_1.svg
AND
JohnS01_1.pdf

## Data Transfer

Transfer both the SVG and PDF file to a USB flash drive.

# 3. Test-cut

This is a recommended but optional step.

Before cutting the keyguard out of plastic, it is helpful to test the fit to see how well the design matches up on the device and how well the openings match up to the buttons on the application. To quickly and inexpensively test the fit, we can laser cut the keyguard out of cardstock or cardboard.

## Laser Test Cut

Bring the USB stick with the PDF design file to the laser cutter.

## Assessing Fit

The keyguard should sit flat on the touchscreen. A little wiggle room is better than too tight. The openings should match up with the buttons

## Refinements

If necessary, adjust the size and spacing so the keyguard fits the device and matches the buttons properly.

# 4. Final Cut

## Final Design Checks

□ | If possible, have you cut a design to test the fit?
□ | Are the corners rounded?
□ | Is the keyguard marked with makersmakingchange.com ?
□ | Is the keyguard marked with any requests from the user (name, app, etc)?

## Laser Cutting

Bring the USB flash drive with the final design files to the laser cutter so the keyguard can be cut out of acrylic.

# 5.Finishing

There are a few final steps to make the keyguard ready for use.

## Smoothing

Check to make sure there are no sharp edges on the keyguard outline or any of the openings. A sharp knife or small file can be used to smooth over any sharp edges.

## Mounting

There are a few different methods for mounting a keyguard on to an AAC device including:
- suctions cups
- velcro
- suction tape
- magnets
- under the case

Suction tape (or "suction cup tape") bonds to smooth, flat, clean surfaces just like a suction cup. Though not actually suction cups, the surface of this tape has thousands of microscopic craters that work by creating many partial vacuums between the tape and the target surface.

The tape is not pressure sensitive, can re-bond repeatedly, and leaves no residue on the target surface. To remove, you simply pull the tape off or twist it to break the bond.

1. Cut some narrow strips of suction tape.
2. Attach the strips of suction tape to the edges of the keyguard.

# Appendix

## iPad Screenshot Scaling

To capture a screenshot on an iPad device, load the app and hold the device in the desired orientation. While holding down the On/Off button, press the Home button. The screen will flash to indicate a screenshot has been captured.

The screenshot image will be 1024 pixels wide and 768 pixels high regardless of the actual size of the screen on the device. In order to scale it properly, use the conversion factor in the table below.

iPad Type | Screen Width (mm) | Screen Height (mm) | Conversion (px to mm)
iPad | 198.1 | 149 | 0.193
iPad2 | 198.1 | 149 | 0.193
iPad 3rd generation | 198.1 | 149 | 0.193
iPad 4th generation | 198.1 | 149 | 0.193
iPad 5th generation | 196.47 | 147.39 | 0.192
iPad Pro 9.7-inch | 203.11 | 153.71 | 0.198
iPad Pro 10.5-inch | 213.5 | 160.13 | 0.208
iPad Pro 12.9-inch 1st Generation | 262.27 | 196.61 | 0.256
iPad Pro 12.9-inch 2nd Generation | 262.27 | 196.61 | 0.256
iPad mini | 161.2 | 121.3 | 0.157
iPad mini 2 | 161.2 | 121.3 | 0.157
iPad mini 3 | 161.2 | 121.3 | 0.157
iPad mini 4 | 161.24 | 121.31 | 0.157
iPad Air | 198.1 | 149 | 0.193
iPad Air 2 | 203.11 | 153.71 | 0.198

Source: http://volksswitch.org/index.php/volks-devices/fully-customizable-3d-printable-aac-keyguard-for-tablets/using-app-screenshots-to-determine-the-app-layout/ (http://volksswitch.org/index.php/volks-devices/fully-customizable-3d-printable-aac-keyguard-for-tablets/using-app-screenshots-to-determine-the-app-layout/)

## Fusion 360 Workflow

Autodesk Fusion 360 is a cloud-based, computer-assisted design program with a free license for hobbyists and enthusiasts. Fusion 360 requires a 64 bit system and either Windows or MAC OS. To access the hobbyist license, you’ll need to sign up for an account and download the free trial: https://www.autodesk.com/products/fusion-360/overview

Fusion 360 has a few features that make it a useful tool for designing custom laser cut keyguards.

Insert Canvas
1. Under the insert menu, select Insert Canvas
2. Choose the top plane
3. Select the image
4. Rotate the image to align the edges with the grid. You may need to manually enter a small value (e.g. 1, 0.1 degrees) into the box.

Scale the Image
1. In the Browser bar, click the triangle beside the Canvasses Folder to show its contents
2. Right click on the canvas image you added in the previous step and select ‘Calibrate Image’
3. Use the mouse to select a first and a second point on the image with a known distance between them, and then enter the distance value in to the dialog box. Try to be as accurate as possible when entering the points so the reference image is scaled properly.

Design Keyguard Layout
1. Create a new sketch on the same plane as the canvas.
2. Create the outline of the keyguard using the rectangle tool.
3. Create the keyguard button openings using rectangles or circles according to the users preference.
4. When finished, close the sketch.

Tip #1: Use construction lines to help align the openings.

Tip #2: To make the design symmetric, add a construction line in the middle and use the Sketch>Mirror tool to copy openings to the other side. You can also use Symmetry constraints to enforce symmetry.

Extrude Keyguard Sketch
1. Click Create > Extrude
2. Select the keyguard profile sketch.
3. Set the extrusion distance to 1/16 inch or 1/8 inch

Export sketch

1. Right click on the sketch
2. Click ‘Save as DXF’

Import sketch into Inkscape
1. Import the dxf file.
2. In some cases the design may be upside down. You may need to rotate the design 180 degrees.
3. Add any marking or text.
4. Change the line color and stroke according to the laser cut file preparation instructions.

## Additional Resources

Suction Tape
http://www.keyguardat.com/suction-tape/

3D Printed Keyguard Workflow http://volksswitch.org/index.php/volks-devices/fully-customizable-3d-printable-aac-keyguard-for-tablets/ (http://volksswitch.org/index.php/volks-devices/fully-customizable-3d-printable-aac-keyguard-for-tablets/)

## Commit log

2018-08-27 Update README.md
    Add tables of device links
2019-03-01 Lasercut Keyguard Instructions 1-1
    This update has users take a screen shot of the app they are using to help ensure good layout and accurate measurements of the keyguard.
2019-04-24 Added keyboard template for lenovo thinkpad x1 carbon 6th-gen
    [arc.scad, thinkpad-x1-carbon-6th-gen.dxf, thinkpad-x1-carbon-6th-gen.scad]
